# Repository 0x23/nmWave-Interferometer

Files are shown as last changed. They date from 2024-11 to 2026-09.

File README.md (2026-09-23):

# An Open Source Interferometer for Accurate Distance Measurements

The goal of this project is to provide plans and techniques for building an interferometer that can accurately measure changes in distance over a range of hundreds of millimeters with sub-micrometer precision. The objective is to use low-cost, widely available components and achieve a good balance between ease of manufacturing and performance.

This repository is currently work in progress...

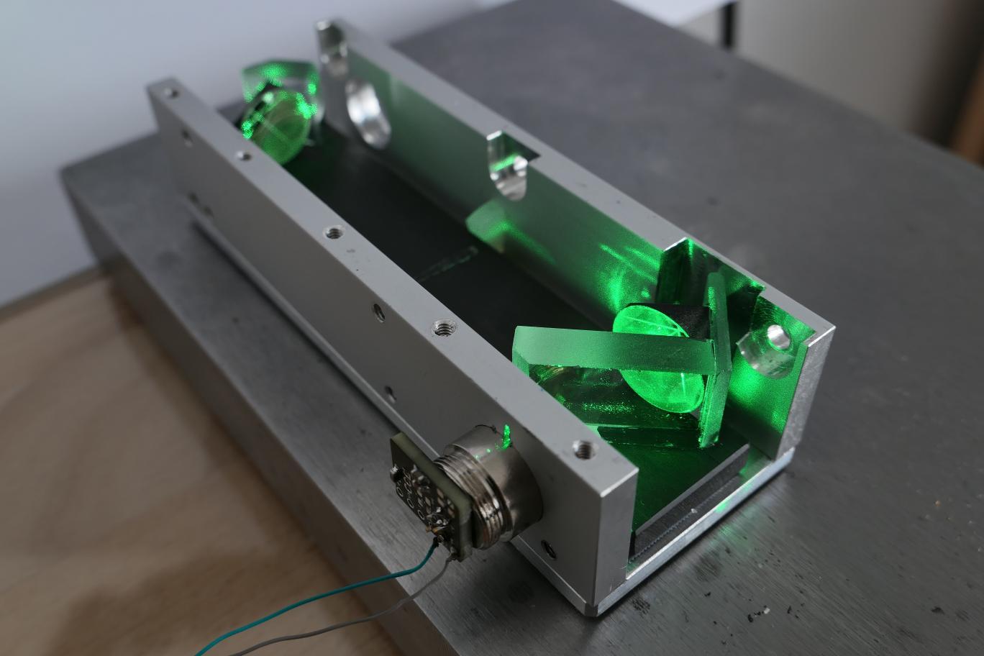
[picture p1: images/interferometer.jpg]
Interferometer


> [!WARNING]
>
> This project involves collimated laser beams with power levels above eye-safe limits able to cause permanent eye damage.
> Please use proper precautions, do your own research, and respect laser safety guidelines.
>
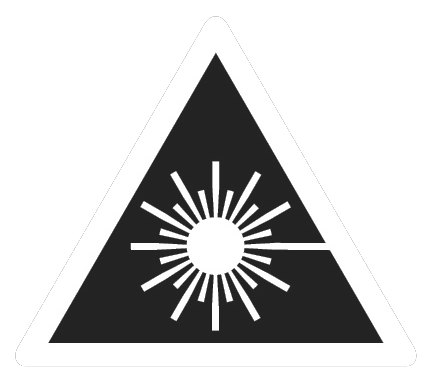
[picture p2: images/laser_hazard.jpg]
Laser Hazard
> 

[3D-Printed Grinding Tools](tools_3dprinted/beam_splitter_22mmx13mm)

## Electronics

The KICAD design files for the electronics have been updated to the newest development version. The design is still work in progress but all functions have been successfully tested on a prototype. 

<div style="display: flex; gap: 2%;">
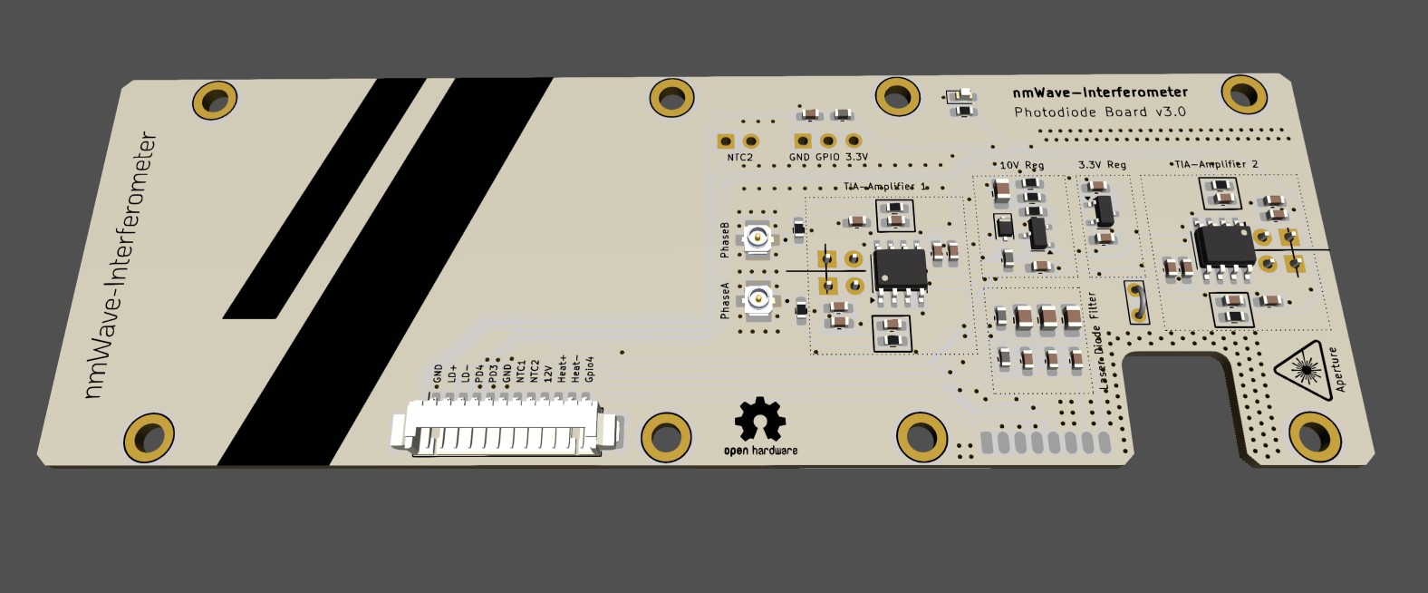
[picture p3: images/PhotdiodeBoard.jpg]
  
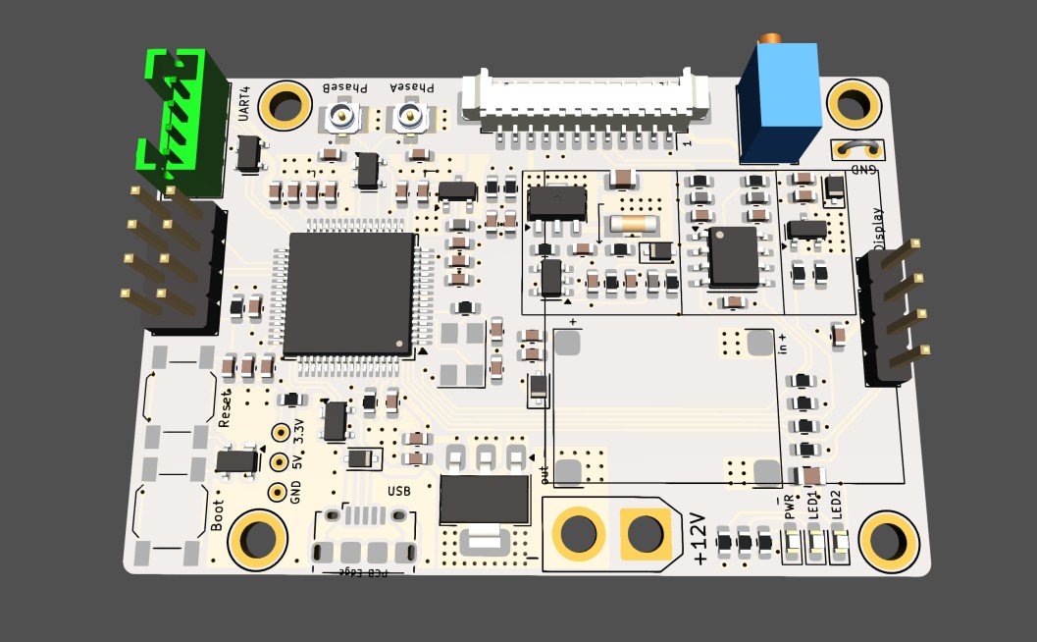
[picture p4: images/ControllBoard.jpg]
  
</div>

<!-- <img src="images/ControllBoardLayout.jpg" alt="Photodiode Board" height="200"/> -->

## CAD Models

[NEW DESIGN - Version 5] FreeCAD models of the design are now online, take a look! 

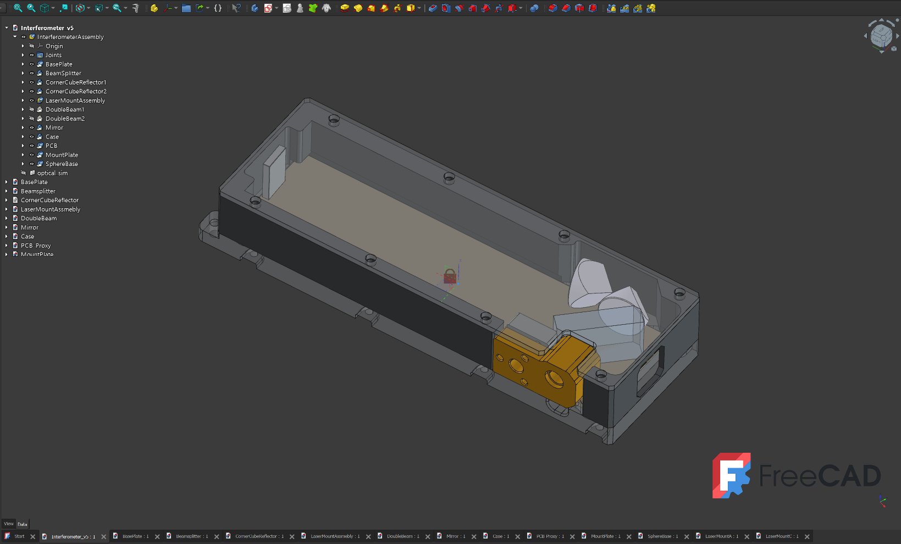
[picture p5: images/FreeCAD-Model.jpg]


## Beam Splitter

The Beam splitter is made from regular float glass with a thickness of about 6 mm. It does not requre any coatings and uses the inherent reflectivity of glass surfaces.
It is ground to size using a diamond wetstone and a series of 3D printed jigs. The models for 3d printing can be found here:

## Laser Diodes

The current recommandation is the: $${\color{lightgreen}Osram \space PLT5 \space 516FA}$$ costing about 12$

For this project the laser source requires a long coherence length, which only certain laser diode models can provide.
Below is a table of laser diodes that I tested or want to test in future:
<br><br>

| Part Number           | Nominal Current | Optimal Drive Current | Power   | Wavelength  | Notes                                             | Plus on case |
|-----------------------|-----------------|-----------------------|---------|-------------|---------------------------------------------------|-----------|
| SLD3232VF             | 55mA            | ?                     | 50mW    | 405nm       | Not good                                          | Yes       |
| QL65E7SA              | 50mA            | 30mA                  | 7mW     | 650nm       | Good                                              | Yes       |
| QL65E7SB or C         | 50mA            | 30mA                  | 7mW     | 650nm       | Good                                              | Yes       |
| PLT520B               | 225mA           | ?                     | 110mW   | 520nm       | Very good (coherence length >4m)                  | Yes       |
| PLT5 516FA            | 100mA           | 36mA                  | 30mW    | 516nm       | (Very) good (CURRENT CHOICE)                      | No        |
| PLT5 520EB_Q          | -               | ?                     | 20mW    | 520nm       | Not tested (datasheet suggests very good)         | No        |
| PLT5 450(G)B          | 80mA            | 21mA                  | 100mW   | 450nm       | Okay                                              | No        |
| PLT5 520DB            | -               | ?                     | 10mW    | 520nm       | Not tested (probably not good)                    | No        |
| PLT5 518FB_P          | -               | ?                     | 30mW    | 518nm       | Not tested (probably not good)                    | No        |

## Photo Diodes

For the project fast photodiodes for the visible spectral range are required. Silicon PIN Photodiodes satisfy these requirements and are readily available.
To get a good signal a small active area of about 1mm² without a lens is prefereable. 

The current choice is the $${\color{lightgreen}SFH229}$$ photodiode in a 3mm LED casing costing about 0.70$.

It is sensitive in the range of 380 nm bis 1100 nm and has a switching time of 10ns. To to reduce the footprint and remove the lense a 3D printed jig and sandpaper can be used.
Mor information on this subject is coming soon..

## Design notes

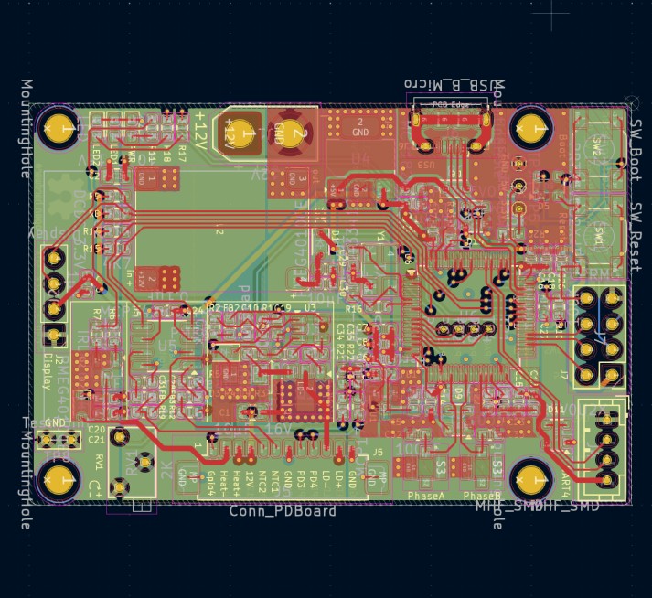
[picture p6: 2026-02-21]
images/ControllBoardLayout.jpg

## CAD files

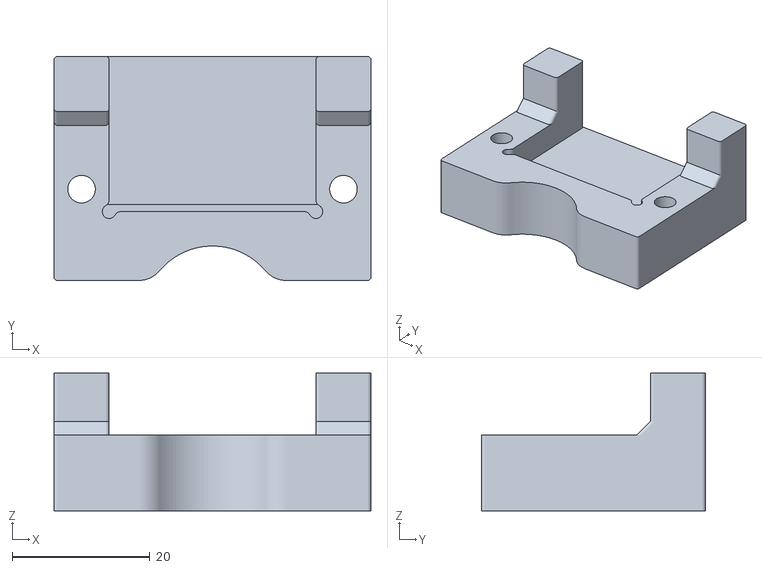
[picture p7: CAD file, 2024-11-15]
tools_3dprinted/beam_splitter_22mmx13mm/BeamSplitter_GrindingFixture_22.4mm.obj
46.0 x 32.5 x 20.0

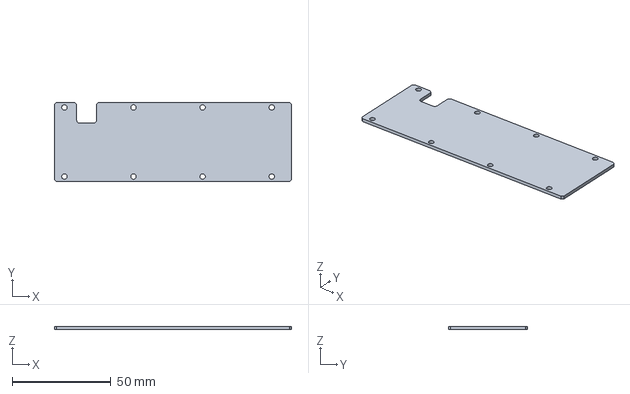
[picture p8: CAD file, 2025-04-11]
construction/PCB-Proxy.FCStd
120.0 x 40.0 x 1.60 mm

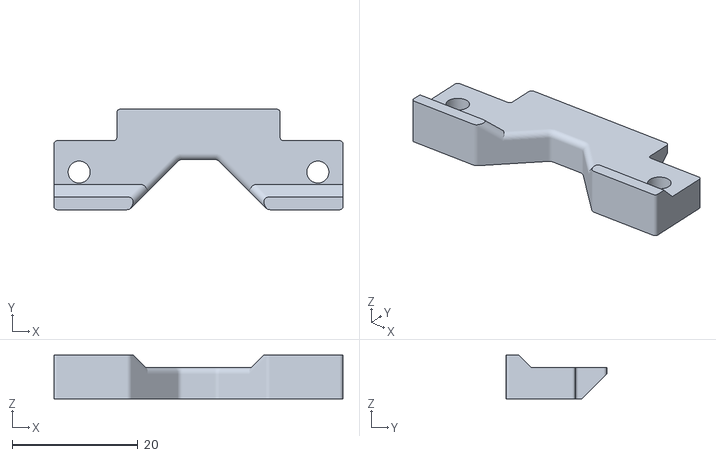
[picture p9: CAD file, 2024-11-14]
tools_3dprinted/beam_splitter_22mmx13mm/BeamSplitter_GrindingFixture_Clamp.obj
46.0 x 16.0 x 7.00

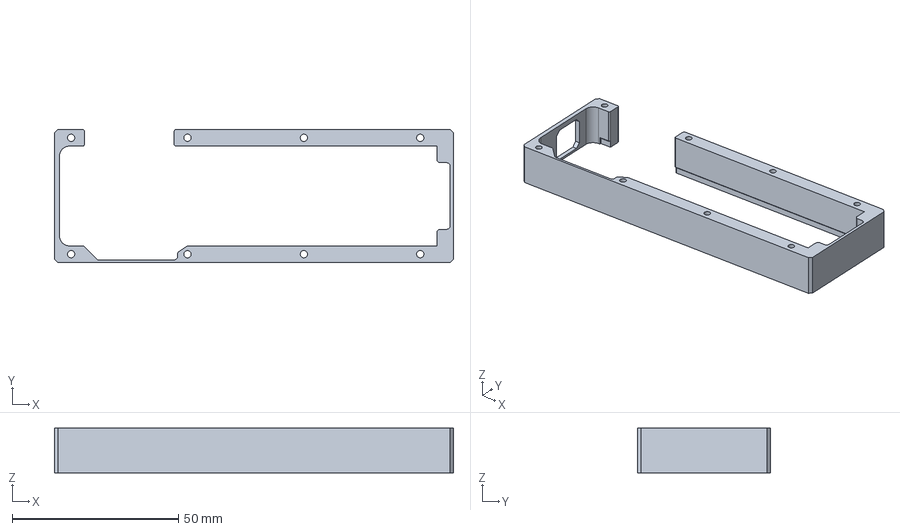
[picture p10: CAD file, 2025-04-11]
construction/Case.FCStd
120.0 x 40.0 x 13.5 mm

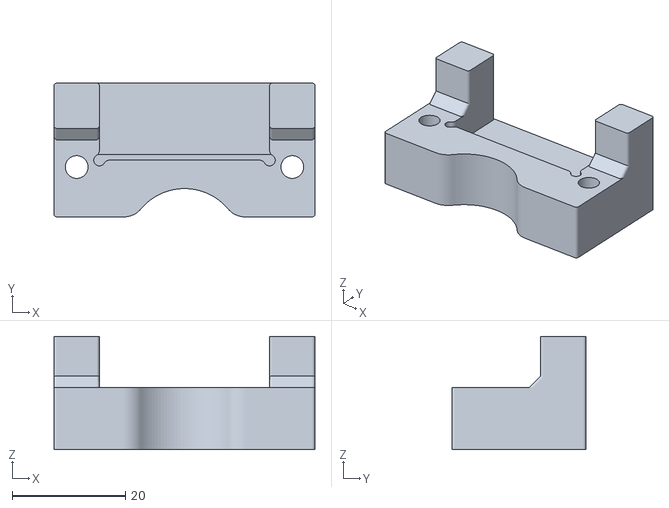
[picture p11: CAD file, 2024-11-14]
tools_3dprinted/beam_splitter_22mmx13mm/BeamSplitter_GrindingFixture_13.6mm.obj
46.0 x 23.6 x 20.0

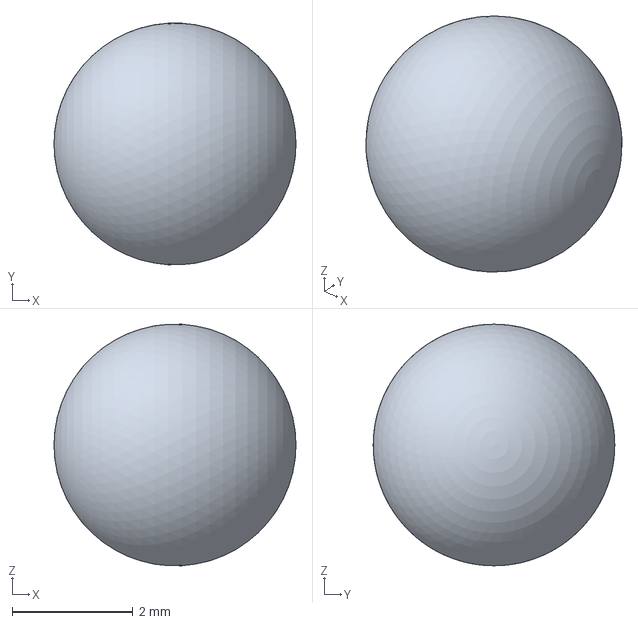
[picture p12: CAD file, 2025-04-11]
construction/SphereBase.FCStd
4.00 x 3.99 x 3.99 mm

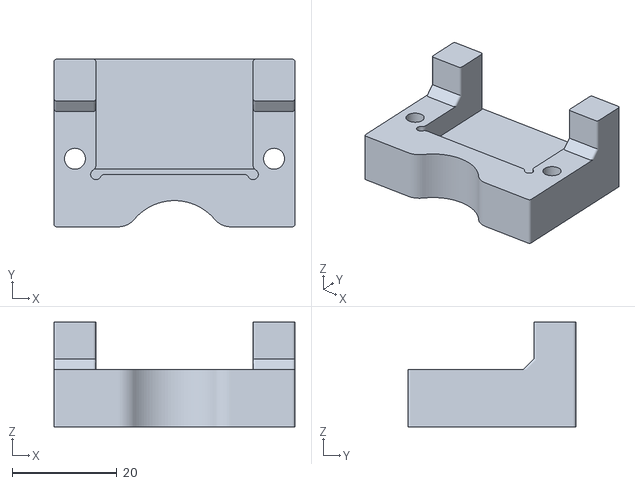
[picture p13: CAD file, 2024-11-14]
tools_3dprinted/beam_splitter_22mmx13mm/BeamSplitter_GrindingFixture_22.0mm.obj
46.0 x 32.0 x 20.0

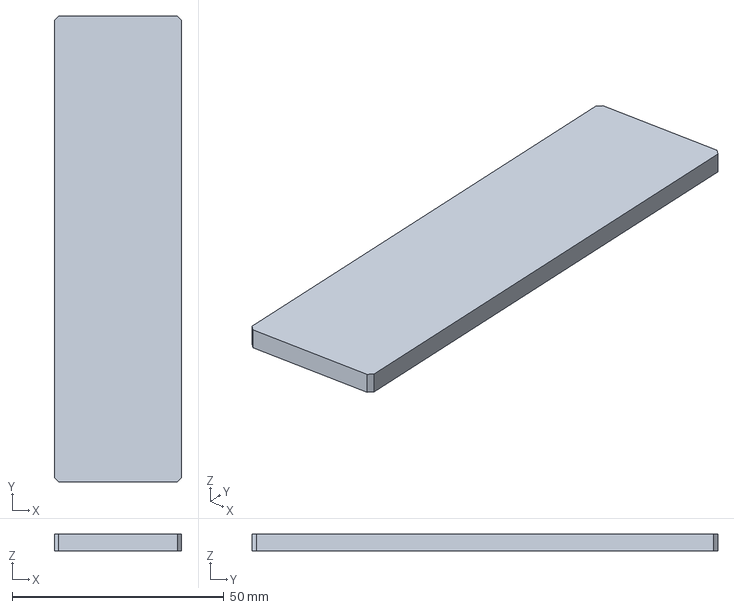
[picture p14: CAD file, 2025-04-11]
construction/BasePlate.FCStd
30.0 x 110.0 x 4.00 mm

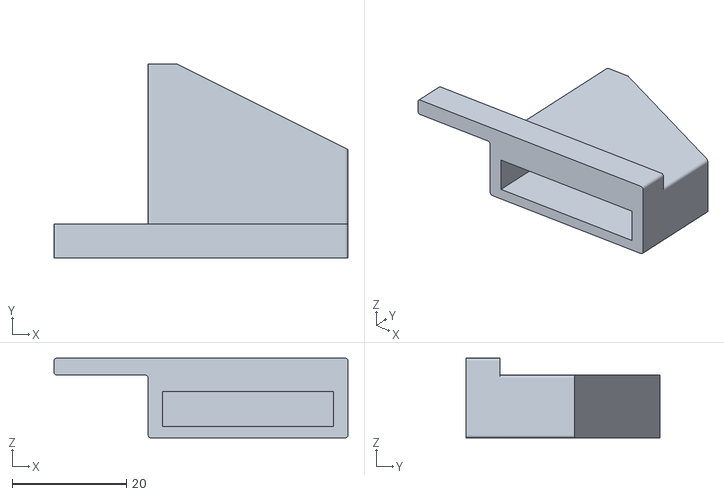
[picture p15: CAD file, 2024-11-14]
tools_3dprinted/beam_splitter_22mmx13mm/BeamSplitter_ScroingJig_14mm.obj
51.5 x 34.0 x 14.0

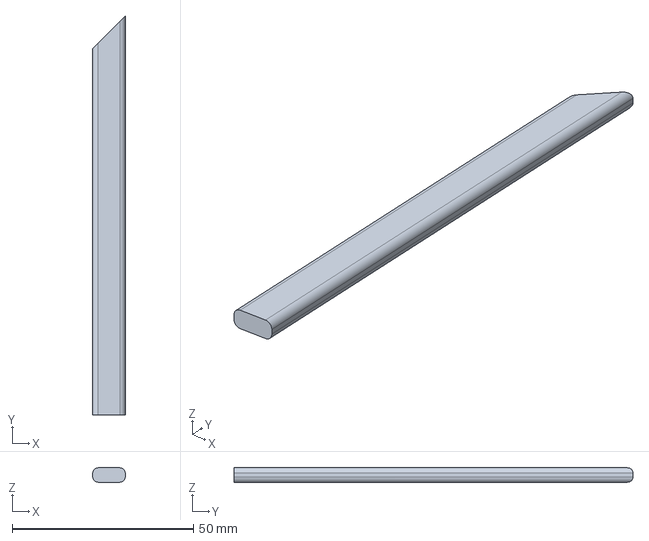
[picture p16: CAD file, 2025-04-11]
construction/DoubleBeam.FCStd
9.00 x 110.0 x 4.00 mm

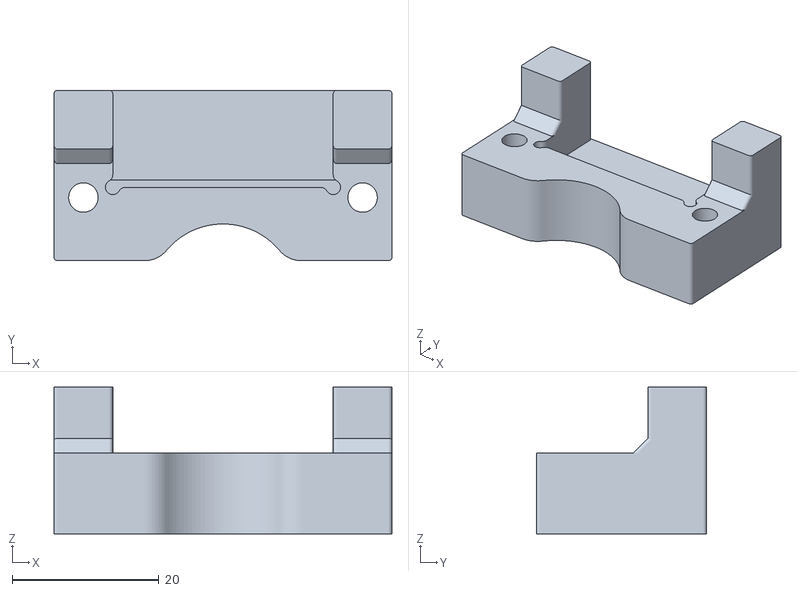
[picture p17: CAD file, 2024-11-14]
tools_3dprinted/beam_splitter_22mmx13mm/BeamSplitter_GrindingFixture_13.2mm.obj
46.0 x 23.2 x 20.0

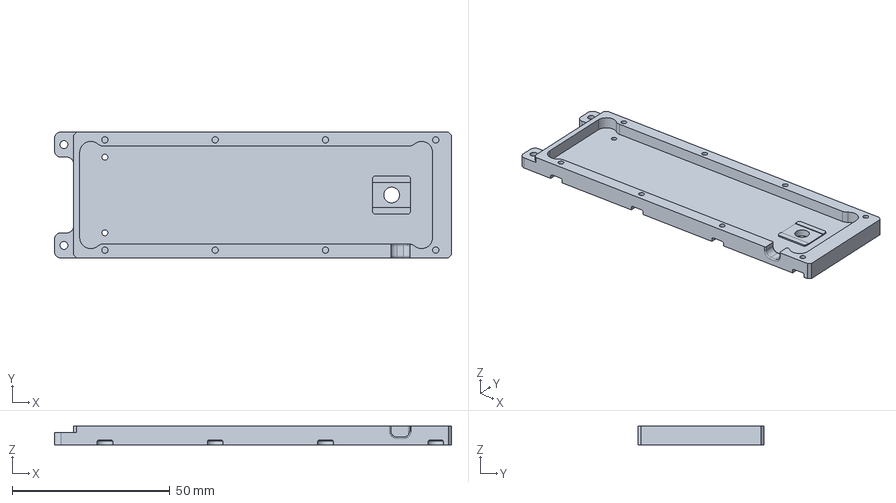
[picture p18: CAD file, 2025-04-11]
construction/MountPlate.FCStd
126.0 x 40.0 x 6.00 mm

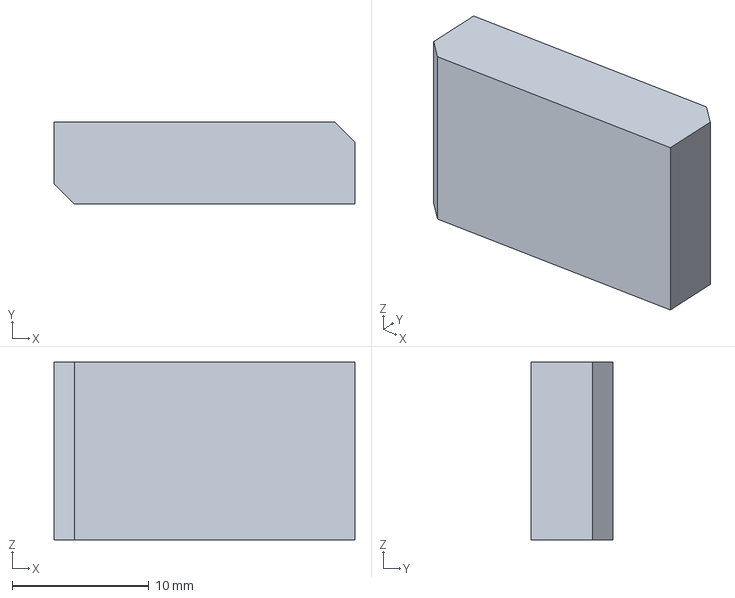
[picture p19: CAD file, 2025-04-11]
construction/Beamsplitter.FCStd
22.0 x 6.00 x 13.0 mm

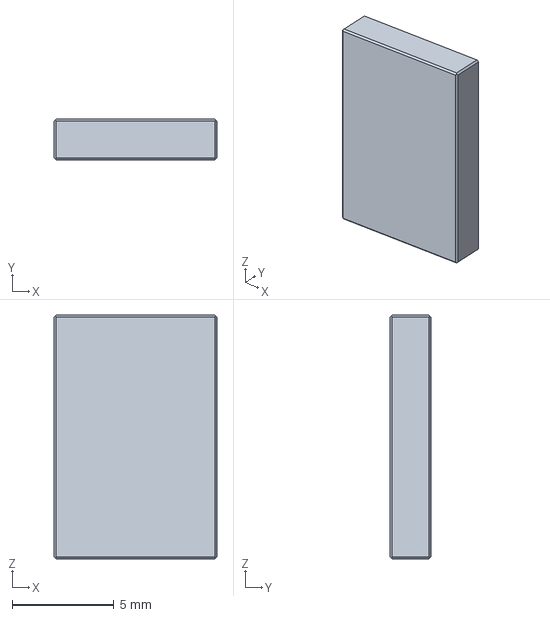
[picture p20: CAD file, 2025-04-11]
construction/Mirror.FCStd
8.00 x 2.00 x 12.0 mm

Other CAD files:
construction/CCRAssembly.FCStd
construction/Interferometer_v5.FCStd
construction/LaserMountAssmebly.FCStd
construction/OpticalLayoutTemplate.FCStd
construction/CCRMount.FCStd
construction/CCRMount2.FCStd
construction/CornerCubeReflector.FCStd
construction/Interferometer.FCStd
construction/LD_MountingTool.FCStd
construction/LaserMountA.FCStd
construction/LaserMountC.FCStd
construction/MirrorMountingTool.FCStd

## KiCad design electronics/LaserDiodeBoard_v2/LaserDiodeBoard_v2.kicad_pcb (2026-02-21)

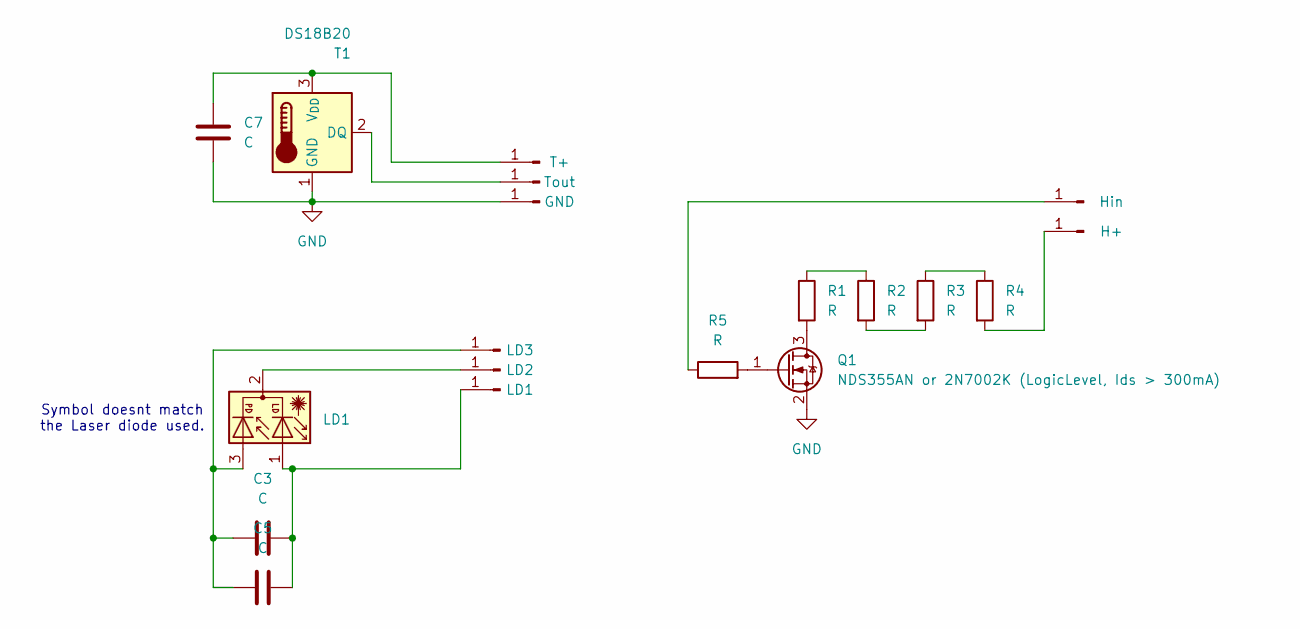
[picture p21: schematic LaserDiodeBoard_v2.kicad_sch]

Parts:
C3, C5, C7: C; C_0603_1608Metric_Pad1.08x0.95mm_HandSolder
J1: H+; SolderWirePad_1x01_SMD_1x2mm
J2: Hin; SolderWirePad_1x01_SMD_1x2mm
J3: LD3; SolderWirePad_1x01_SMD_1x2mm
J4: LD2; SolderWirePad_1x01_SMD_1x2mm
J5: LD1; SolderWirePad_1x01_SMD_1x2mm
J6: GND; SolderWirePad_1x01_SMD_1x2mm
J7: Tout; SolderWirePad_1x01_SMD_1x2mm
J8: T+; SolderWirePad_1x01_SMD_1x2mm
LD1: LD; LaserDiode_TO18-D5.6-3
Q1: NDS355AN or 2N7002K (LogicLevel, Ids > 300mA); SOT-23
R1, R2, R3, R4: R; R_0805_2012Metric_Pad1.20x1.40mm_HandSolder
R5: R; R_0603_1608Metric_Pad0.98x0.95mm_HandSolder
T1: DS18B20; TO-92_Inline

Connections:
GND: C7.2, J6.1, Q1.2 (S), T1.1 (GND)
unnamed: J1.1, R4.2
unnamed: J2.1, R5.1
unnamed: C3.1, C5.1, J3.1, LD1.3
unnamed: J4.1, LD1.2
unnamed: C3.2, C5.2, J5.1, LD1.1
unnamed: J7.1, T1.2 (DQ)
unnamed: C7.1, J8.1, T1.3 (V_{DD})
unnamed: Q1.3 (D), R1.2
unnamed: Q1.1 (G), R5.2
unnamed: R1.1, R2.1
unnamed: R2.2, R3.2
unnamed: R3.1, R4.1

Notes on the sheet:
Symbol doesnt match the Laser diode used.

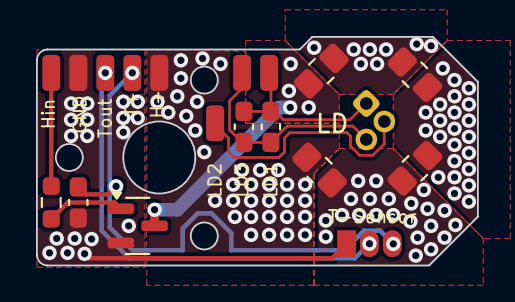
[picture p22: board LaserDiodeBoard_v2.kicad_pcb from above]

Board: 2 copper layers, 24.5 x 12.7 mm, 19 parts (1 on the bottom side), 13 nets.

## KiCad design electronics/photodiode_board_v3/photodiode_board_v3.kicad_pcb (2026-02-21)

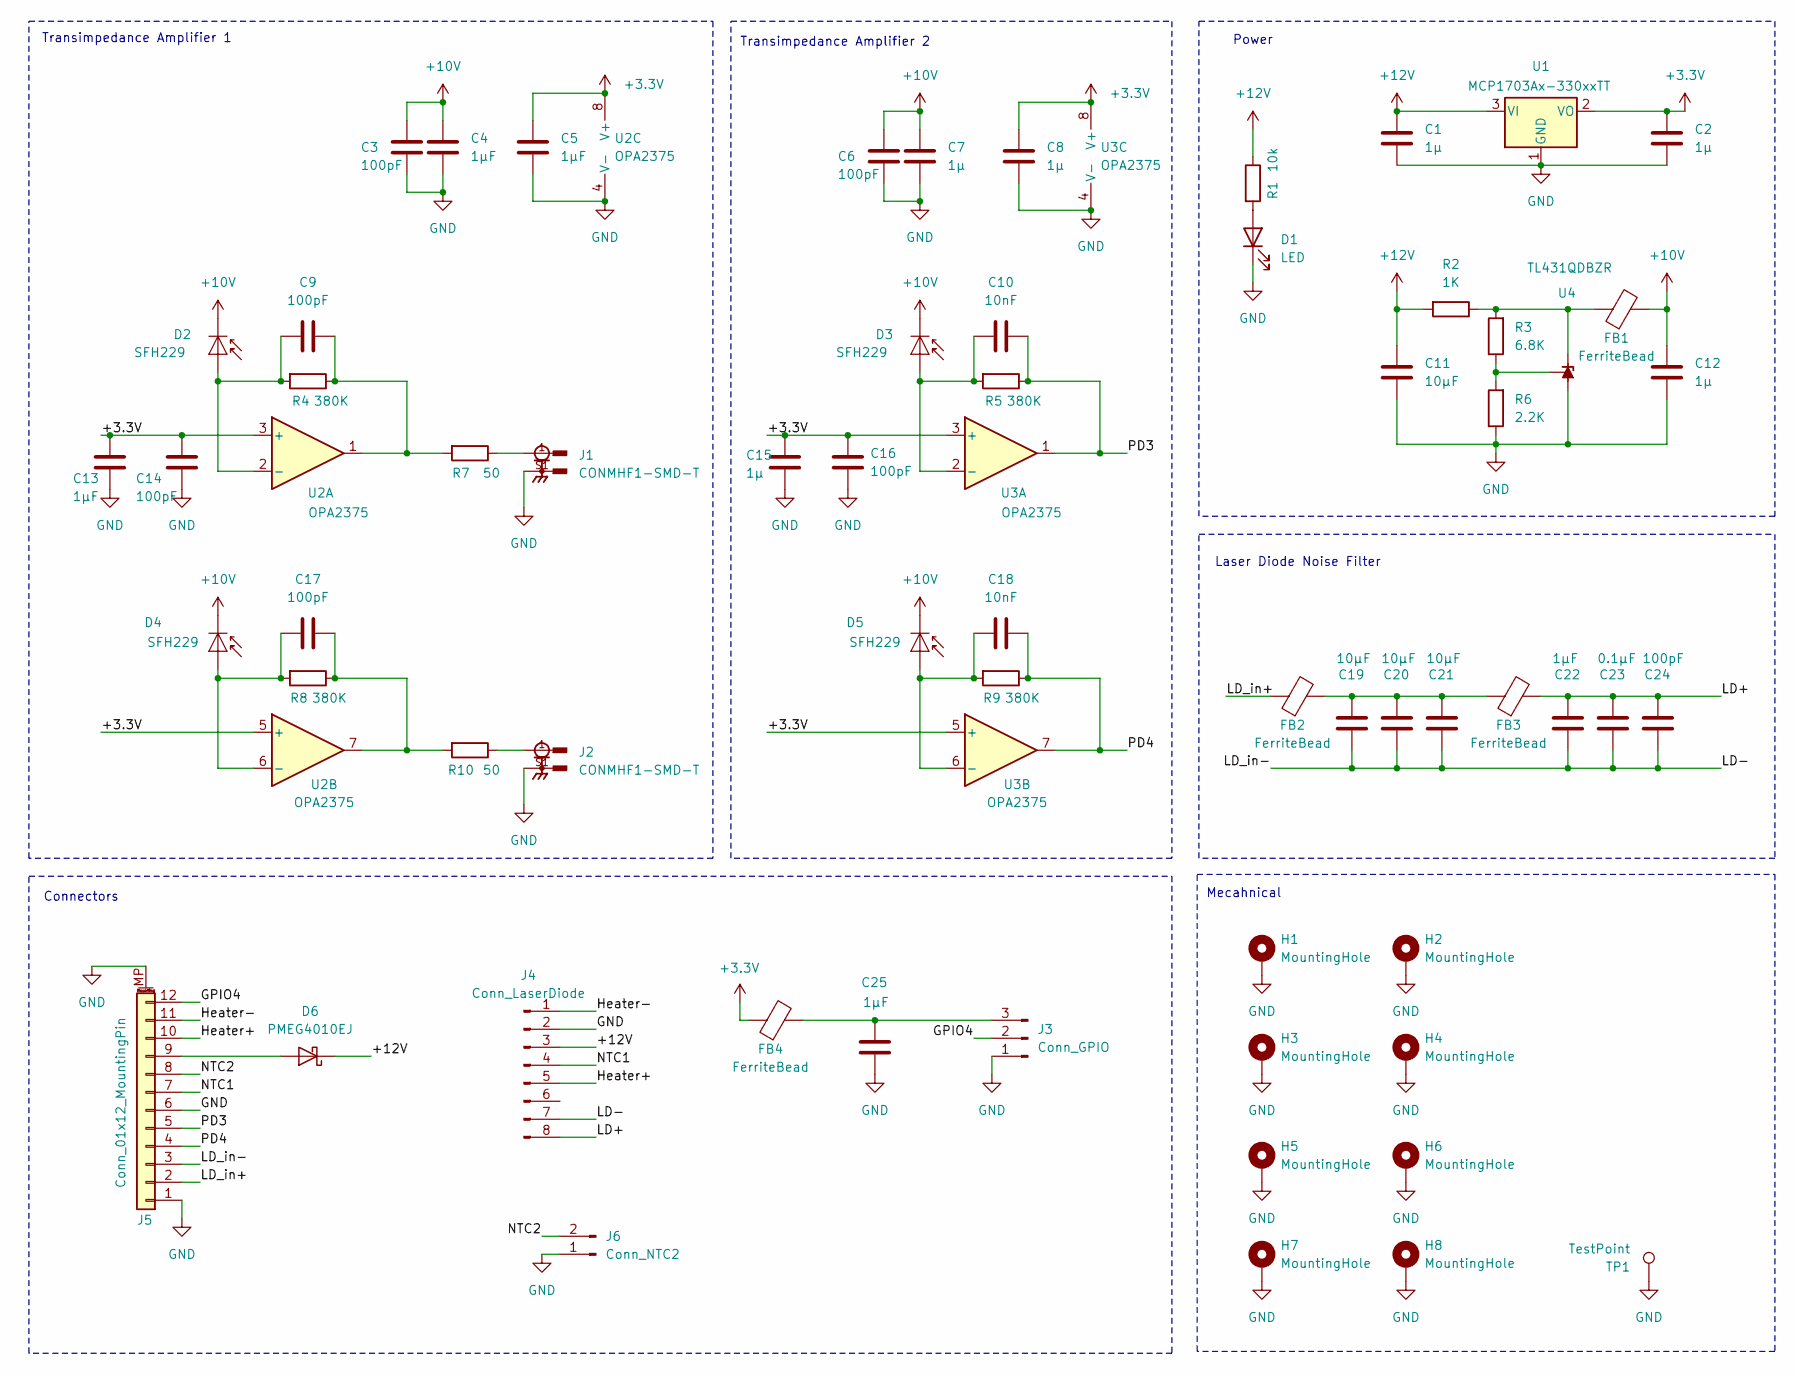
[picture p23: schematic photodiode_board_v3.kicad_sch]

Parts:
C1, C2, C7, C8, C12, C15: 1µ; C_0603_1608Metric_Pad1.08x0.95mm_HandSolder
C3, C6, C9, C14, C16, C17, C24: 100pF; C_0603_1608Metric_Pad1.08x0.95mm_HandSolder
C4, C5, C13, C22, C25: 1µF; C_0603_1608Metric_Pad1.08x0.95mm_HandSolder
C10, C18: 10nF; C_0603_1608Metric_Pad1.08x0.95mm_HandSolder
C11, C19, C20, C21: 10µF; C_0805_2012Metric_Pad1.18x1.45mm_HandSolder
C23: 0.1µF; C_0603_1608Metric_Pad1.08x0.95mm_HandSolder
D1: LED; LED_0603_1608Metric_Pad1.05x0.95mm_HandSolder
D2, D3, D4, D5: SFH229; LED_D3.0mm
D6: PMEG4010EJ; D_SOD-323F
FB1, FB2, FB3, FB4: FerriteBead; L_0603_1608Metric
H1, H2, H3, H4, H5, H6, H7, H8: MountingHole; MountingHole_2.7mm_M2.5_ISO7380_Pad
J1, J2: CONMHF1-SMD-T; LINX_CONMHF1-SMD-T
J3: Conn_GPIO; PinHeader_1x03_P2.54mm_Vertical
J4: Conn_LaserDiode; JST_ZH_B8B-ZR_1x08_P1.50mm_Vertical
J5: Conn_01x12_MountingPin; Molex_PicoBlade_53261-1271_1x12-1MP_P1.25mm_Horizontal
J6: Conn_NTC2; PinHeader_1x02_P2.54mm_Vertical
R1: 10k; R_0603_1608Metric_Pad0.98x0.95mm_HandSolder
R2: 1K; R_0603_1608Metric_Pad0.98x0.95mm_HandSolder
R3: 6.8K; R_0603_1608Metric_Pad0.98x0.95mm_HandSolder
R4, R5, R8, R9: 380K; R_0603_1608Metric_Pad0.98x0.95mm_HandSolder
R6: 2.2K; R_0603_1608Metric_Pad0.98x0.95mm_HandSolder
R7, R10: 50; R_0603_1608Metric_Pad0.98x0.95mm_HandSolder
TP1: TestPoint; TestPoint_Bridge_Pitch2.54mm_Drill0.7mm
U1: MCP1703Ax-330xxTT; SOT-23
U2, U3: OPA2375; SOIC-8_3.9x4.9mm_P1.27mm
U4: TL431QDBZR; SOT-23

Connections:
+3.3V: C2.1, C5.1, C8.1, C13.1, C14.1, C15.1, C16.1, FB4.1, U1.2 (VO), U2.3 (+), U2.5 (+), U2.8 (V+), U3.3 (+), U3.5 (+), U3.8 (V+)
+10V: C3.1, C4.2, C6.1, C7.2, C12.1, D2.1 (K), D3.1 (K), D4.1 (K), D5.1 (K), FB1.2
+12V: C1.1, C11.1, D6.1 (K), J4.3, R1.1, R2.2, U1.3 (VI)
/GPIO4: J3.2, J5.12
/Heater+: J4.5, J5.10
/Heater-: J4.1, J5.11
/LD+: C22.2, C23.2, C24.2, FB3.2, J4.8
/LD-: C19.1, C20.1, C21.1, C22.1, C23.1, C24.1, J4.7, J5.3
/LD_in+: FB2.1, J5.2
/NTC1: J4.4, J5.7
/NTC2: J5.8, J6.2
/PD3: C10.2, J5.5, R5.1, U3.1
/PD4: C18.2, J5.4, R9.1, U3.7
GND: C1.2, C2.2, C3.2, C4.1, C5.2, C6.2, C7.1, C8.2, C11.2, C12.2, C13.2, C14.2, C15.2, C16.2, C25.1, D1.1 (K), H1.1, H2.1, H3.1, H4.1, H5.1, H6.1, H7.1, H8.1, J1.S1, J2.S1, J3.1, J4.2, J5.1, J5.6, J5.MP (MountPin), J6.1, R6.1, TP1.1, U1.1 (GND), U2.4 (V-), U3.4 (V-), U4.3 (A)
unnamed: C9.2, R4.1, R7.2, U2.1
unnamed: C17.2, R8.1, R10.2, U2.7
unnamed: C19.2, C20.2, C21.2, FB2.2, FB3.1
unnamed: D1.2 (A), R1.2
unnamed: C9.1, D2.2 (A), R4.2, U2.2 (-)
unnamed: C10.1, D3.2 (A), R5.2, U3.2 (-)
unnamed: C17.1, D4.2 (A), R8.2, U2.6 (-)
unnamed: C18.1, D5.2 (A), R9.2, U3.6 (-)
unnamed: D6.2 (A), J5.9
unnamed: J1.1, R7.1
unnamed: J2.1, R10.1
unnamed: C25.2, FB4.2, J3.3
unnamed: FB1.1, R2.1, R3.2, U4.1 (K)
unnamed: R3.1, R6.2, U4.2 (REF)

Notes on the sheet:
Transimpedance Amplifier 2
Transimpedance Amplifier 1
Connectors
Power
Laser Diode Noise Filter
Mecahnical

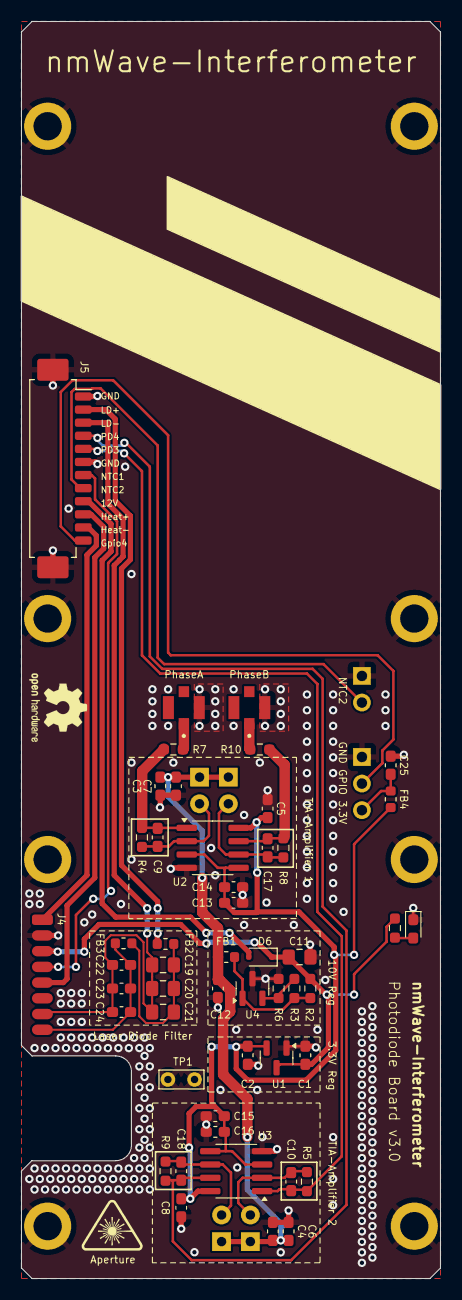
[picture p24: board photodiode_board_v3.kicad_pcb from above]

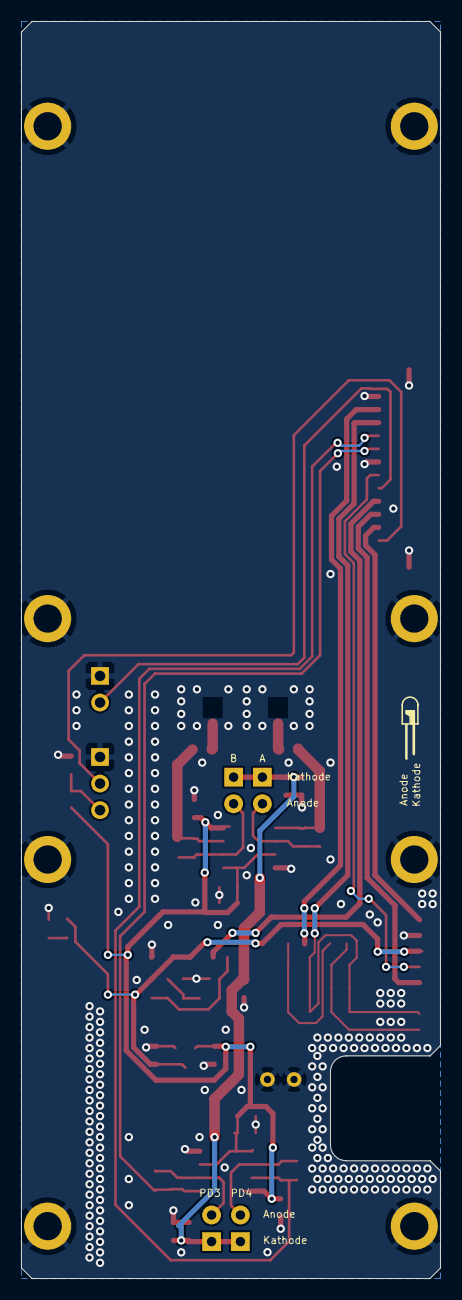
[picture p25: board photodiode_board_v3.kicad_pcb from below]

Board: 2 copper layers, 40.0 x 120.0 mm, 64 parts (4 on the bottom side), 28 nets.

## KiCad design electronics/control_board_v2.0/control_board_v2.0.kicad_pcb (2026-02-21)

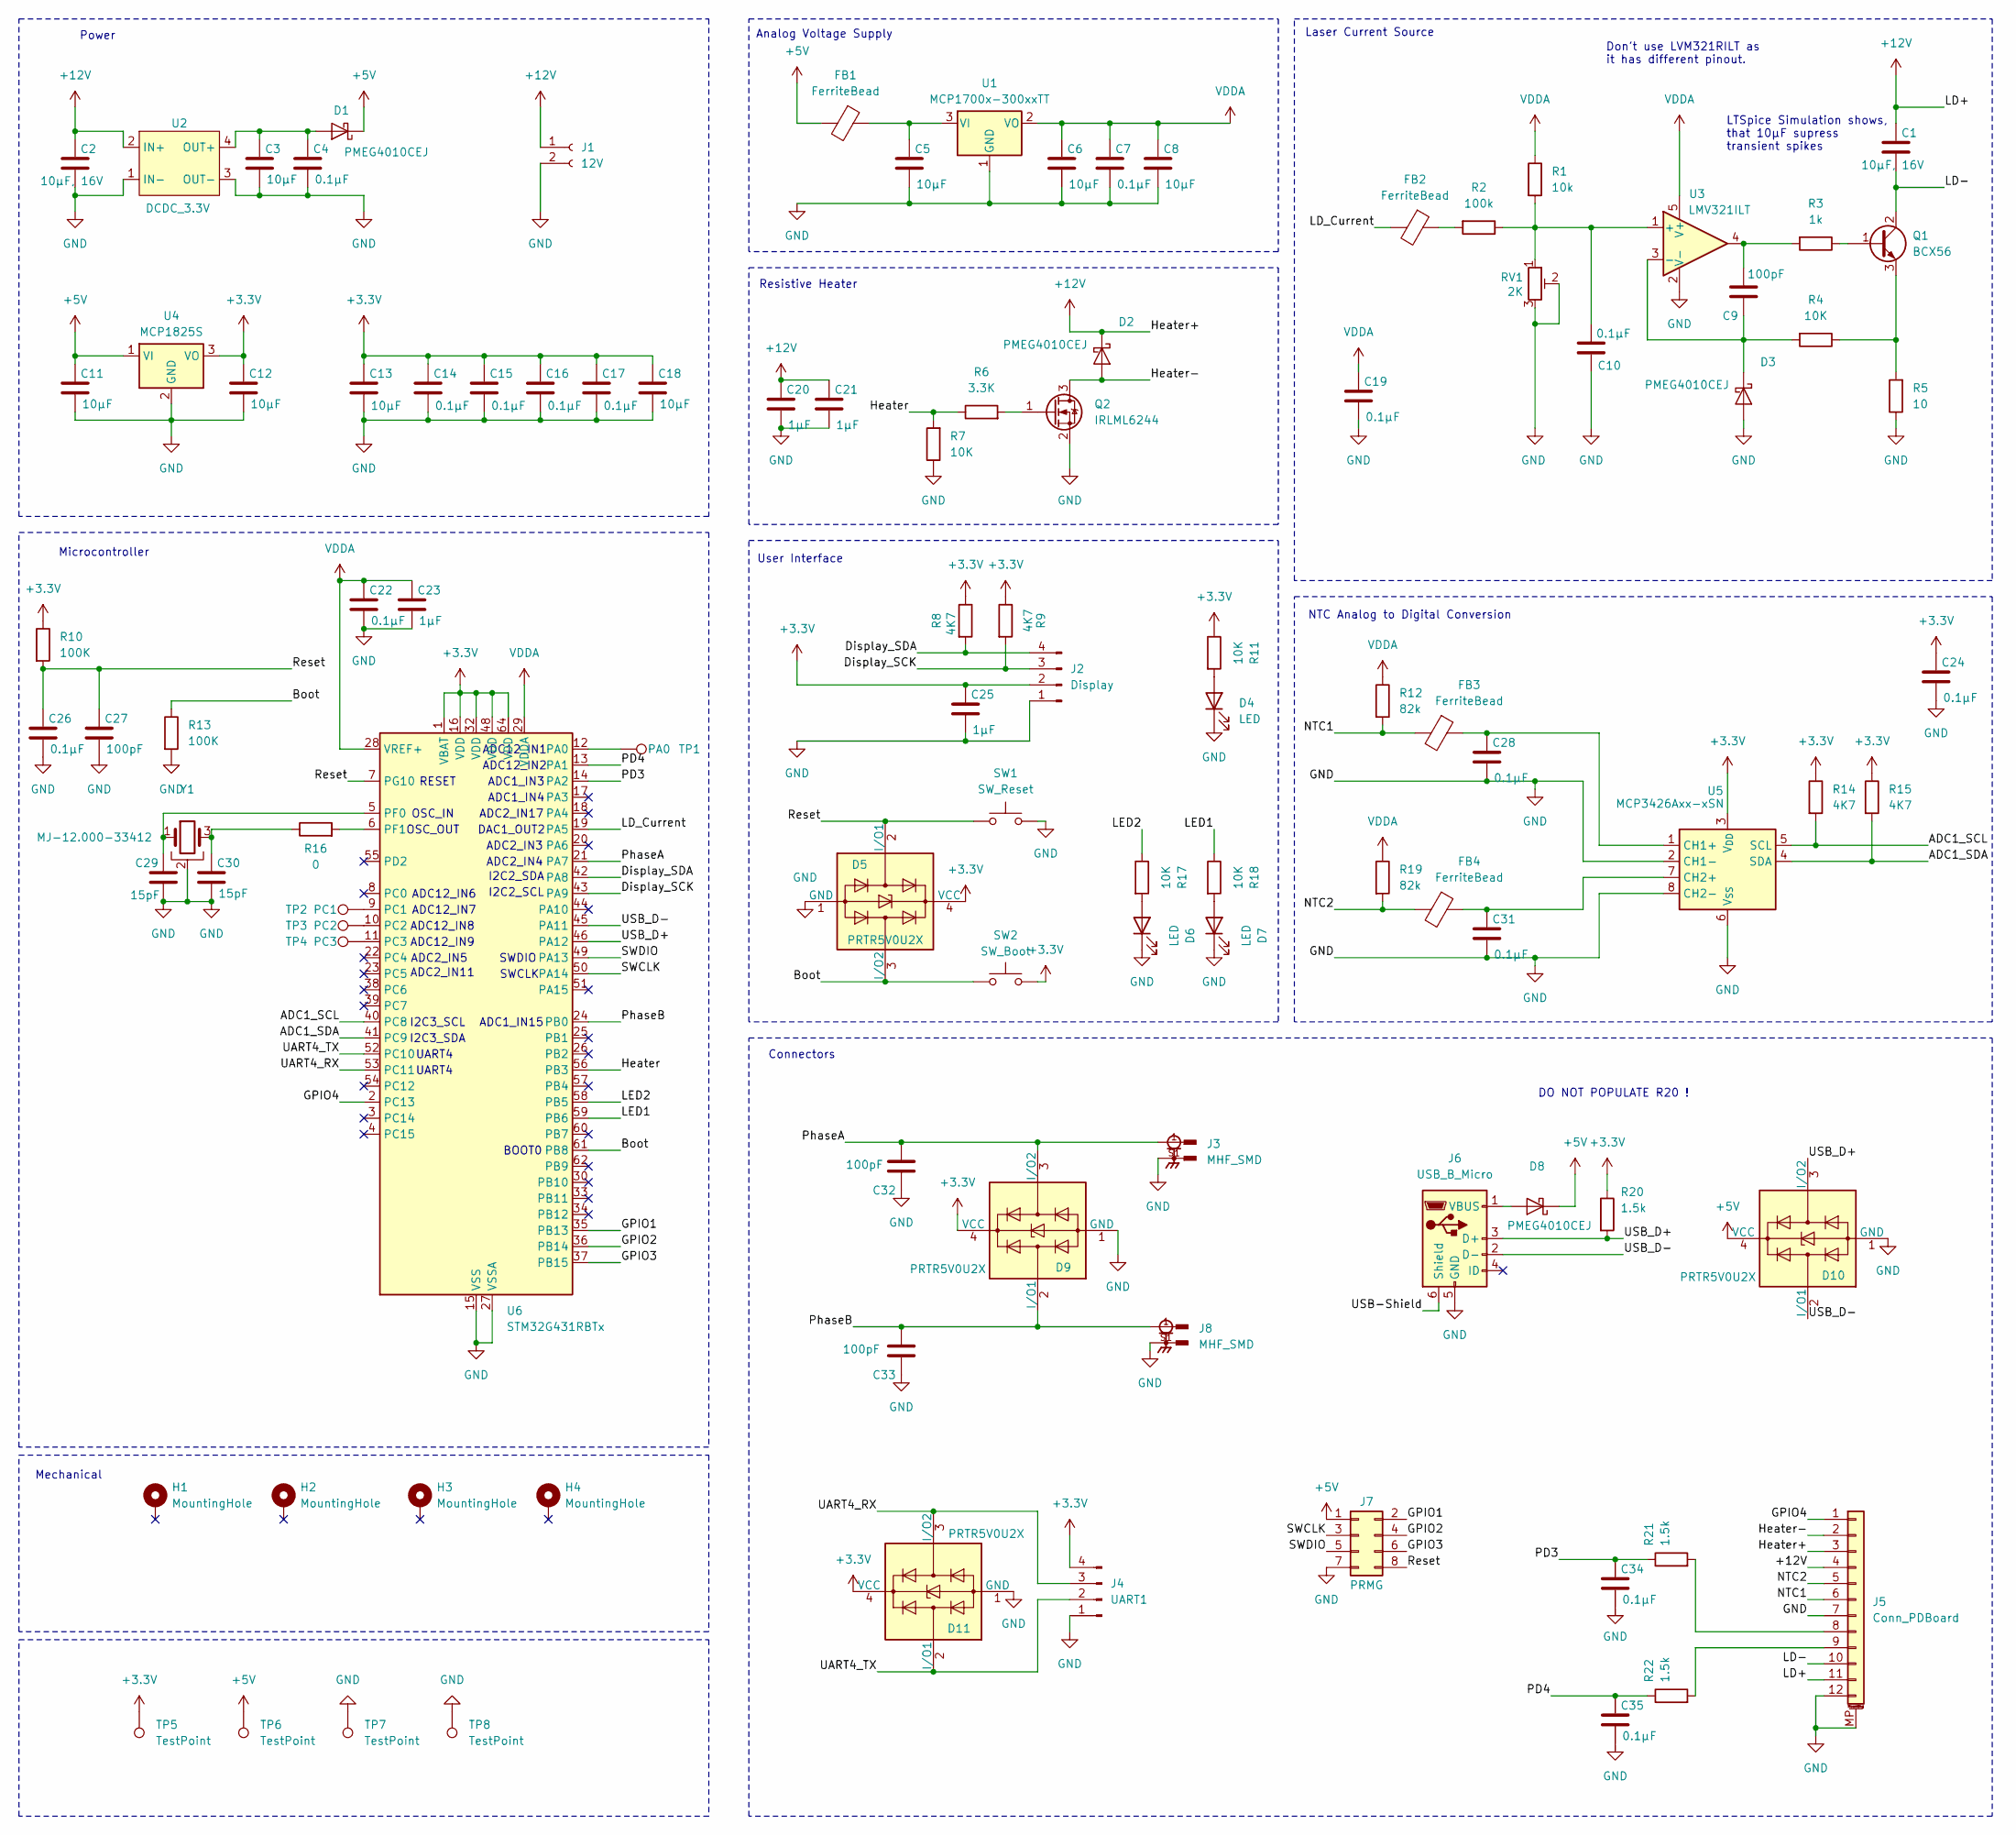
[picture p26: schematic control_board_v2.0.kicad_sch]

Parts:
C1, C2: 10µF, 16V; C_0805_2012Metric
C3, C5, C6, C8, C11, C12, C13, C18: 10µF; C_0603_1608Metric
C4, C7, C10, C14, C15, C16, C17, C19, C22, C24, C26, C28, C31, C34, C35: 0.1µF; C_0603_1608Metric
C9, C27, C32, C33: 100pF; C_0603_1608Metric
C20, C21, C23, C25: 1µF; C_0603_1608Metric
C29, C30: 15pF; C_0603_1608Metric
D1, D2, D3, D8: PMEG4010CEJ; D_SOD-323F
D4, D6, D7: LED; LED_0603_1608Metric_Pad1.05x0.95mm_HandSolder
D5, D9, D10, D11: PRTR5V0U2X; SOT-143
FB1, FB2, FB3, FB4: FerriteBead; L_0603_1608Metric
H1, H2, H3, H4: MountingHole; MountingHole_2.7mm_M2.5_ISO14580_Pad
J1: 12V; AMASS_XT30U-F_1x02_P5.0mm_Vertical
J2: Display; PinHeader_1x04_P2.54mm_Vertical
J3, J8: MHF_SMD; LINX_CONMHF1-SMD-T
J4: UART1; JST_PH_B4B-PH-K_1x04_P2.00mm_Vertical
J5: Conn_PDBoard; Molex_PicoBlade_53261-1271_1x12-1MP_P1.25mm_Horizontal
J6: USB_B_Micro; USB_Micro-B_Amphenol_10118194_Horizontal
J7: PRMG; PinHeader_2x04_P2.54mm_Vertical
Q1: BCX56; SOT-89-3
Q2: IRLML6244; SOT-23
R1: 10k; R_0603_1608Metric
R2: 100k; R_0603_1608Metric
R3: 1k; R_0603_1608Metric
R4, R7, R11, R17, R18: 10K; R_0603_1608Metric
R5: 10; R_MiniMELF_MMA-0204
R6: 3.3K; R_0603_1608Metric
R8, R9, R14, R15: 4K7; R_0603_1608Metric
R10, R13: 100K; R_0603_1608Metric
R12, R19: 82k; R_0603_1608Metric
R16: 0; R_0603_1608Metric
R20, R21, R22: 1.5k; R_0603_1608Metric
RV1: 2K; Potentiometer_Bourns_3266X_Horizontal
SW1: SW_Reset; SW_SPST_SKQG_WithoutStem
SW2: SW_Boot; SW_SPST_SKQG_WithoutStem
TP1: PA0; TestPoint_THTPad_D1.0mm_Drill0.5mm
TP2: PC1; TestPoint_THTPad_D1.0mm_Drill0.5mm
TP3: PC2; TestPoint_THTPad_D1.0mm_Drill0.5mm
TP4: PC3; TestPoint_THTPad_D1.0mm_Drill0.5mm
TP5, TP6, TP7: TestPoint; TestPoint_THTPad_D1.0mm_Drill0.5mm
TP8: TestPoint; TestPoint_Bridge_Pitch2.54mm_Drill0.7mm
U1: MCP1700x-300xxTT; SOT-23
U2: DCDC_3.3V; DCDC_17mmx12mm
U3: LMV321ILT; SOT-23-5
U4: MCP1825S; SOT-223-3_TabPin2
U5: MCP3426Axx-xSN; SOIC-8_3.9x4.9mm_P1.27mm
U6: STM32G431RBTx; LQFP-64_10x10mm_P0.5mm
Y1: MJ-12.000-33412; Crystal_SMD_5032-4Pin_5.0x3.2mm

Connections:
+3.3V: C12.1, C13.1, C14.1, C15.1, C16.1, C17.1, C18.1, C24.1, C25.1, D5.4 (VCC), D9.4 (VCC), D11.4 (VCC), J2.2, J4.4, R8.1, R9.1, R10.1, R11.1, R14.1, R15.1, R20.1, SW2.2, TP5.1, U4.3 (VO), U5.3 (V_{DD}), U6.1 (VBAT), U6.16 (VDD), U6.32 (VDD), U6.48 (VDD), U6.64 (VDD)
+5V: C11.1, D1.1 (K), D8.1 (K), D10.4 (VCC), FB1.2, J7.1, TP6.1, U4.1 (VI)
+12V: C1.1, C2.1, C20.1, C21.1, D2.1 (K), J1.1, J5.3, J5.4, J5.11, U2.2 (IN+)
/ADC1_SCL: R14.2, U5.5 (SCL), U6.40 (PC8)
/ADC1_SDA: R15.2, U5.4 (SDA), U6.41 (PC9)
/Boot: D5.3 (I/O2), R13.1, SW2.1, U6.61 (PB8)
/Display_SCK: J2.3, R9.2, U6.43 (PA9)
/Display_SDA: J2.4, R8.2, U6.42 (PA8)
/GPIO1: J7.2, U6.35 (PB13)
/GPIO2: J7.4, U6.36 (PB14)
/GPIO3: J7.6, U6.37 (PB15)
/GPIO4: J5.1, U6.2 (PC13)
/Heater: R6.1, R7.2, U6.56 (PB3)
/Heater-: D2.2 (A), J5.2, Q2.3 (D)
/LD-: C1.2, J5.10, Q1.2 (C)
/LD_Current: FB2.2, U6.19 (PA5)
/LED1: R18.1, U6.59 (PB6)
/LED2: R17.1, U6.58 (PB5)
/NTC1: FB3.2, J5.6, R12.2
/NTC2: FB4.2, J5.5, R19.2
/PD3: C34.1, R21.1, U6.14 (PA2)
/PD4: C35.1, R22.1, U6.13 (PA1)
/PhaseA: C32.2, D9.3 (I/O2), J3.1, U6.21 (PA7)
/PhaseB: C33.2, D9.2 (I/O1), J8.1, U6.24 (PB0)
/Reset: C26.1, C27.1, D5.2 (I/O1), J7.8, R10.2, SW1.1, U6.7 (PG10)
/SWCLK: J7.3, U6.50 (PA14)
/SWDIO: J7.5, U6.49 (PA13)
/UART4_RX: D11.3 (I/O2), J4.3, U6.53 (PC11)
/UART4_TX: D11.2 (I/O1), J4.2, U6.52 (PC10)
/USB-Shield: J6.6 (Shield)
/USB_D+: D10.3 (I/O2), J6.3 (D+), R20.2, U6.46 (PA12)
/USB_D-: D10.2 (I/O1), J6.2 (D-), U6.45 (PA11)
GND: C2.2, C3.2, C4.2, C5.2, C6.2, C7.2, C8.2, C10.1, C11.2, C12.2, C13.2, C14.2, C15.2, C16.2, C17.2, C18.2, C19.2, C20.2, C21.2, C22.2, C23.2, C24.2, C25.2, C26.2, C27.2, C28.2, C29.2, C30.2, C31.2, C32.1, C33.1, C34.2, C35.2, D3.2 (A), D4.1 (K), D5.1 (GND), D6.1 (K), D7.1 (K), D9.1 (GND), D10.1 (GND), D11.1 (GND), J1.2, J2.1, J3.S1, J4.1, J5.7, J5.12, J5.MP (MountPin), J6.5 (GND), J7.7, J8.S1, Q2.2 (S), R5.1, R7.1, R13.2, RV1.2, RV1.3, SW1.2, TP7.1, TP8.1, U1.1 (GND), U2.1 (IN-), U2.3 (OUT-), U3.2 (V-), U4.2 (GND), U5.2 (CH1-), U5.6 (V_{SS}), U5.8 (CH2-), U6.15 (VSS), U6.27 (VSSA), U6.31 (VSS), U6.47 (VSS), U6.63 (VSS), Y1.2
unnamed: C9.2, R3.2, U3.4
unnamed: C30.1, R16.1, Y1.3
unnamed: C3.1, C4.1, D1.2 (A), U2.4 (OUT+)
unnamed: C9.1, D3.1 (K), R4.2, U3.3 (-)
unnamed: D4.2 (A), R11.2
unnamed: D6.2 (A), R17.2
unnamed: D7.2 (A), R18.2
unnamed: D8.2 (A), J6.1 (VBUS)
unnamed: FB2.1, R2.2
unnamed: J5.8, R21.2
unnamed: J5.9, R22.2
unnamed: Q1.1 (B), R3.1
unnamed: Q1.3 (E), R4.1, R5.2
unnamed: Q2.1 (G), R6.2
unnamed: C5.1, FB1.1, U1.3 (VI)
unnamed: C10.2, R1.2, R2.1, RV1.1, U3.1 (+)
unnamed: C28.1, FB3.1, U5.1 (CH1+)
unnamed: C31.1, FB4.1, U5.7 (CH2+)
unnamed: TP1.1, U6.12 (PA0)
unnamed: TP2.1, U6.9 (PC1)
unnamed: TP3.1, U6.10 (PC2)
unnamed: TP4.1, U6.11 (PC3)
unnamed: C29.1, U6.5 (PF0), Y1.1
unnamed: R16.2, U6.6 (PF1)
VDDA: C6.1, C7.1, C8.1, C19.1, C22.1, C23.1, R1.1, R12.1, R19.1, U1.2 (VO), U3.5 (V+), U6.28 (VREF+), U6.29 (VDDA)

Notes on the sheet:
SWCLK
ADC1_IN4
Don't use LVM321RILT as it has different pinout.
ADC12_IN8
I2C2_SDA
ADC12_IN2
ADC12_IN7
ADC2_IN17
I2C3_SCL
Laser Current Source
ADC1_IN15
SWDIO
OSC_IN
ADC2_IN11
ADC2_IN3
Resistive Heater
ADC2_IN4
Microcontroller
OSC_OUT
ADC2_IN5
ADC12_IN1
UART4
BOOT0
ADC1_IN3
Power
Mechanical
I2C2_SCL
NTC Analog to Digital Conversion
DO NOT POPULATE R20 !
Connectors
LTSpice Simulation shows, that 10µF supress transient spikes
RESET
ADC12_IN9
Analog Voltage Supply
DAC1_OUT2
User Interface
I2C3_SDA
ADC12_IN6

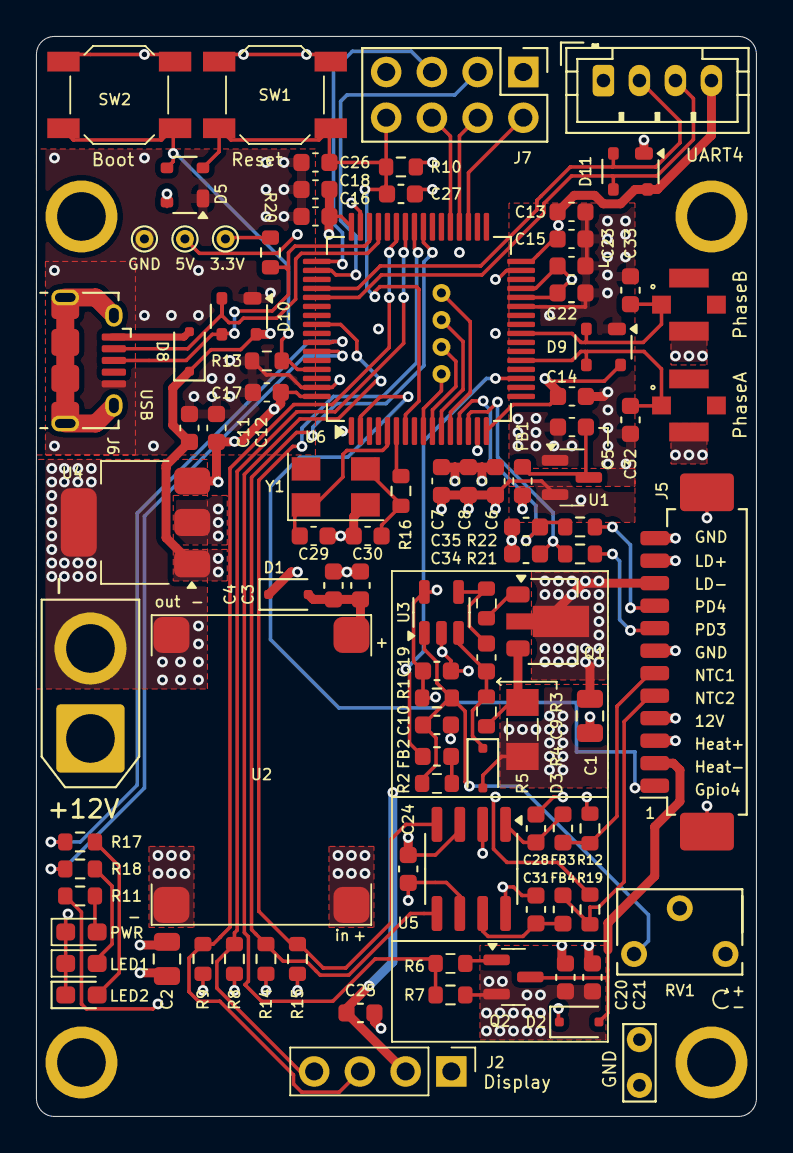
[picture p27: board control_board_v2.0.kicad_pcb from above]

Board: 4 copper layers, 40.0 x 60.0 mm, 104 parts (0 on the bottom side), 57 nets.

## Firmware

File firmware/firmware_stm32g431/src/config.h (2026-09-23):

#define PIN_LED1 PB6
#define PIN_LED2 PB5

#define PIN_PHASE_A PA7   // PhaseA - photo diode input 
#define PIN_PHASE_B PB0   // PhaseB - photo diode input
#define PIN_PHOTODIODE_3 PA2
#define PIN_PHOTODIODE_4 PA1
#define PIN_HEATER PB3

#define ADC1_SCL PC8
#define ADC1_SDA PC9
#define LD_CURRENT PA5    // laser diode current modulation analog out

#define UART4_TX PC10
#define UART4_RX PC11

#define DISPLAY_SDA PA8
#define DISPLAY_SCL PA9

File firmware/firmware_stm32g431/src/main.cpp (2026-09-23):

#include "config.h"
#include "dual_sample_adc.h"
#include "hardware/MCP3426_adc.h"
#include "stm32g4xx_hal.h"
#include "Arduino.h"
#include "Wire.h"
#include "utilities/logging.h"


CDualSampleADC phase_adc(
                        GPIOB, 0, ADC_CHANNEL_15,   // ADC1_IN15
                        GPIOA, 7, ADC_CHANNEL_4
                        );

MCP3426_Adc temperature_adc(PC9, PC8, 0x68); // MCP3426 default address

void blink(int count, int period_ms) {
  for(int i=0; i<count; i++) {
    digitalWrite(PIN_LED1, true);
    delay(period_ms / 2);
    digitalWrite(PIN_LED1, false);
    delay(period_ms / 2); 
  }
}

//extern "C" void SysTick_Handler(void) {
//    HAL_IncTick();
//}

#include <Wire.h>

void i2c_scan(TwoWire &wire) {
  Serial.println("I2C scan...");

  uint8_t count = 0;
  for (uint8_t addr = 1; addr < 127; addr++) {
    wire.beginTransmission(addr);
    if (wire.endTransmission() == 0) {
      Serial.print("Found device at 0x");
      if (addr < 16) Serial.print("0");
      Serial.println(addr, HEX);
      count++;
    }
  }

  if (count == 0)
    Serial.println("No I2C devices found");
}



void setup() {
  Serial.begin(115200);
 // while(!Serial);
  Serial.println("STM32G431 Started...");

  Serial.print("SystemCoreClock: ");
  Serial.println(SystemCoreClock);
  Serial.print("Crystal Freq: ");
  Serial.println(HSE_VALUE);

  // setup temperature adc
  Serial.println("Configure Temperature sensing");
  temperature_adc.begin();
  if(temperature_adc.configure(MCP3426_Adc::GAIN_1, MCP3426_Adc::ONE_SHOT, MCP3426_Adc::RES_16BIT)) 
    Serial.println("[ok]");
  else
    Serial.println("[failed]");
  temperature_adc.start_conversion(MCP3426_Adc::CH1);

  // setup photodiode adc 
  phase_adc.begin();
  analogReadResolution(12);  // STM32 ADC is 12-bit by default, but just in case

  // setup laser current dac 
  pinMode(LD_CURRENT, OUTPUT); 
  analogWriteResolution(12);
  analogWrite(PA5, 1024);

  // --- PWM Configuration (Explicitly specifying PWM functions for clarity) ---
  pinMode(PIN_HEATER, OUTPUT);
  analogWriteFrequency(100);

  analogWrite(PIN_LED1, 20);
  analogWrite(PIN_HEATER, 2048);
}

#include <cmath>

float ntc_voltage_to_temp(float voltage, float R_pullup, float vcc=3.3, float R0 = 100000.0f, float B = 3950.0f) {
    if (voltage >= vcc) voltage = vcc-1e-7f;

    // Step 1: Compute NTC resistance
    float R_ntc = (voltage * R_pullup) / (vcc - voltage);

    // Step 2: Apply Beta formula
    float T0 = 298.15f; // 25°C in Kelvin
    float tempK = 1.0f / ( (1.0f/T0) + (1.0f/B) * log(R_ntc / R0) );

    // Step 3: Convert to Celsius
    float tempC = tempK - 273.15f;
    return tempC;
}


float t = 0.0f;
void loop() {
  uint16_t phase_a=0, phase_b=0;
  phase_adc.read(&phase_b, &phase_a);

 // phase_a = analogRead(PIN_PHASE_A);
 // phase_b = analogRead(PIN_PHASE_B);
  //phase_a = ADC1_Read();

  analogWrite(PA5, int(sin(t*5.0f)*128+2048));

  float tv = 0.0f;
  //temperature_adc.start_conversion(MCP3426_Adc::CH1);
  //delay(100);
  if(temperature_adc.read_voltage(tv)) {
    temperature_adc.start_conversion(MCP3426_Adc::CH1);
    tv = ntc_voltage_to_temp(tv, 82000);
    Serial.print(">T: ");
    Serial.println(tv, 12);
  }

  Serial.print(">PhaseA: ");
  Serial.println(phase_a);
  Serial.print(">PhaseB: ");
  Serial.println(phase_b);  
  // Serial.println("");  
  delay(10);
  t += 0.01f;
}

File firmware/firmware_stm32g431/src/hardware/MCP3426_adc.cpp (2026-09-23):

#include "MCP3426_adc.h"

#include "MCP3426_adc.h"

MCP3426_Adc::MCP3426_Adc(int pin_sda, int pin_scl, uint8_t address)
    : m_i2c(pin_sda, pin_scl), m_address(address), m_config(0), m_scale(1), m_scale_voltage(1), m_resolution(RES_16BIT)
{}

void MCP3426_Adc::begin() {
    m_i2c.setClock(400000); // 400 kHz
    m_i2c.begin();
}

bool MCP3426_Adc::configure(Gain gain, Mode mode, Resolution res) {
    m_config = 0;
    m_config |= (gain & 0x03);        // bits 0-1: G1-G0 PGA gain
    m_config |= (res & 0x03) << 2;    // bits 2-3: S1-S0 sample rate / resolution
    m_config |= (mode & 0x01) << 4;   // bit 4: O/C conversion mode
    m_config |= 0x80;                 // bit 7 RDY=1 starts conversion (one-shot mode)


    m_resolution = res;
    switch (m_resolution) {
      case RES_12BIT: m_scale = 1.0f/(1<<11); break;
      case RES_14BIT: m_scale = 1.0f/(1<<13); break;
      case RES_16BIT: m_scale = 1.0f/(1<<15); break;
    }

    float v_ref=2.048f;
    switch (gain) {
      case GAIN_1: m_scale_voltage = v_ref*m_scale; break;
      case GAIN_2: m_scale_voltage = v_ref*m_scale*2; break;
      case GAIN_4: m_scale_voltage = v_ref*m_scale*4; break;
      case GAIN_8: m_scale_voltage = v_ref*m_scale*8; break;
    }

    return write_config();
}

bool MCP3426_Adc::start_conversion(Channel channel) {
    m_config &= ~0x10;               // clear channel bit
    if (channel == CH2)
        m_config |= 0x10;

    m_config |= 0x80;                // RDY=1 to start conversion
    return write_config();
}

bool MCP3426_Adc::read_raw(int16_t &value) {
    m_i2c.requestFrom((int)m_address, 3);
    if (m_i2c.available() < 3) return false; // conversion not ready

    uint8_t msb = m_i2c.read();
    uint8_t lsb = m_i2c.read();
    uint8_t config = m_i2c.read();

    m_config = config;
    if (config & 0x80) return false; // RDY=1 → not ready

    value = ((uint16_t)msb << 8) | lsb;
    return true;
}

bool MCP3426_Adc::read(float &v) {
    int16_t raw;
    if (!read_raw(raw)) return false;

    v = float(raw) * m_scale;
    return true;
}

// Read voltage in range -1 to 1 (non-blocking), returns true if a new value is available
bool MCP3426_Adc::read_voltage(float& voltage) {
    int16_t raw;
    if (!read_raw(raw)) return false;

    voltage = float(raw) * m_scale_voltage;
    return true;
}

bool MCP3426_Adc::write_config() {
    m_i2c.beginTransmission(m_address);
    m_i2c.write(m_config);
    return m_i2c.endTransmission() == 0;
}

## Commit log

2024-11-14 added 3d printed tools
    [BeamSplitter_GrindingFixture_13.2mm.obj, BeamSplitter_GrindingFixture_13.6mm.obj, BeamSplitter_GrindingFixture_22mm.obj, BeamSplitter_ScroingJig_14mm.obj]
2024-11-14 added images
    [BeamSplitter_GrindingFixture_Clamp.obj]
2024-11-15 added tool mesh
    [BeamSplitter_GrindingFixture_22.0mm.obj, BeamSplitter_GrindingFixture_22.4mm.obj]
2025-03-19 FreeCAD files of new design added
    [BasePlate.FCStd, Beamsplitter.FCStd, CCRAssembly.FCStd, CCRMount.FCStd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]
2025-04-11 new mechanical design (version 5)
    [BasePlate.FCStd, Beamsplitter.FCStd, Case.FCStd, DoubleBeam.FCStd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]
2025-04-18 added first version of the base board for community review
2025-04-18 added missing cad file
    [Interferometer_v5.FCStd]
2025-09-03 board review files
2026-02-21 Added current version of electronics. Its still work in progress.
    [LaserDiodeBoard_v2.kicad_pcb, LaserDiodeBoard_v2.kicad_sch, control_board_v2.0.kicad_pcb, control_board_v2.0.kicad_sch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]
